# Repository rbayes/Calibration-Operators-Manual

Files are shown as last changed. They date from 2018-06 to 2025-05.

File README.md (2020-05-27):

# Calibration-Operators-Manual
An update to the calibration operator procedures for SNO+

Suggestions/Issues/Plans

Front Matter, (title page, linked table of contents) needs to be added.

May need to re-assess organisation of sections

## 2. Controls
- needs to be updated for the current calibration computer
- login information (passwords?)
- manmon (for external systems)

## 3. Manipulator
- needs update for hanger/bellows systems
- external systems (possibly) need to be highlighted
- double check that the computer system description is up to date

## 4. Manipulator Geometry
- Review "Global Coordinate System"
  - are all of the tables complete?
  - are they still correct?
- Does the context of the global geometry still make sense
  - Going from a UI mounted system to a I-beam mounted system
  - Should calibration system be defined wrt the PSUP
- Glovebox and UI description should be borrowed from the detector paper (early drafts)

## 5. Calibration Gas Systems
- Will need to have some comments about the cover gas system
- Specifications and UI cover gas monitoring will be required
  - Borrow from the detector paper and the TWiki
- Plans for URM cover gas required
- Comments on background mitigations and radon requirements

## 6. Laser
- Is the existing documentation sufficient
- Super Nova Calibration source?

## 7. Sources
- Need Scintillator sources (Laserball AmBe, Tagged, Untagged and Cherekov sources)
- Need external source specifications (AmBe, N16, Laserball)

## 8. Procedures
- Should separate Water Only, Scintillator Only, External and Generally applicable procedures into different sections
- Water Only
  - Mounting procedures
  - Internal N16 deployment
- External Deployment Procedures (Needs to be brought up to standards)
  - Mounting procedures (to be written)
  - N16
  - AmBe
  - Laserball 
- Scintillator (with adjustments)
  - Mounting procedures
  - Pump/purge procedures 
  - Cover gas maintenance
  - Source handling
  - AmBe / Encapsulated deployments (adapted from water) 
  - Cherenkov deployment (adapted from water)
  - Laserball deployments (adapted from water) 
- Applicable to all
  - Supernova source
  - DT generator
  - Laser procedures
  
## 9. Deployment Records?
- Would it be worth recording Run numbers, dates, run plans in the operators manual for future reference?
- Limit to one page summaries

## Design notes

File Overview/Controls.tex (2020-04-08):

Control of the calibration manipulator and the calibration laser is
done through the \textbf{calibration} computer running the \textbf{manip}
program which is a C++ program running on Linux. There are three ways
for the operator to send commands to \textbf{manip}:
\begin{itemize}
\item From the \textbf{calibration} console in the DCR.
\item From the \textbf{manmon} program running on a number of Linux
  boxes.
\end{itemize}
When changing source or adjusting equipment in the DCR, the console is
usually used. Otherwise the calibration operator usually interacts
with the manipulator through \textbf{manmon}. The manipulator can be
operated both from underground or from surface without any personnel
in the lab. There is also a monitoring program running on
\textbf{buffer1.sp.snolab.ca}. This program is called
\textbf{manip\_logger} which generates a json document containing the
current manipulator status and uploads the result to a couch database
on the \textbf{snopl.us} server. The resulting files may be viewed
from a web browser or downloaded directly.

\section{Controlling and Monitoring the Manipulator from manmon}
Nominal operatiorn of the mainipulator is through \textbf{manmon}
which is a Tcl/Tk program which runs on various Linux workstations on
site. Specifically the workstations

\paragraph{monug1} The workstation in the underground control room.
\paragraph{monag1} The workstation in the surface control room.
\paragraph{monlu1} The workstation in the Laurentian control room.

\textbf{manmon} provides a GUI interface to display the manipulator
data and to allow the Calibration Operator to move sources or operate
the calibration laser.

\subsection{Starting manmon}
\begin{enumerate}
\item Log on to \textbf{monug1} as \textbf{snoperator}
\item Go to the current manmon directory.
\begin{verbatim}
cd ~/manmon_3.00
\end{verbatim}
\item Start the \textbf{manmon} program by typing
\begin{verbatim}
manmon
\end{verbatim}
A GUI user interface will pop up Fig.~\ref{fig:manmonGUI}.
\item The GUI connects to the calibration computer automatically, but
  in case it does not, the connection may be forced by clicking on the
  \textbf{connect} button. A window will pop up (see
  Fig.\ref{fig:connect}) 
\end{enumerate}
The procedure is identical in the other control rooms.

\section{Controlling the Manipulator from the Console}
On the calibration computer, change to the directory
\begin{verbatim}
~/AVR32
\end{verbatim}
and run the program
\begin{verbatim}
./manip
\end{verbatim}
The basic commands are:
\paragraph{help}
\paragraph{list} lists all objects
\paragraph{logout} disconnects the tcp/ip connection
\paragraph{quit} exists program
Commands for the \verb+prototyp+ object (typically a source object
like \verb+laserball+, \verb+ambe+, \verb+li8+, etc.)

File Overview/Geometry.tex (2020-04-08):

\section{SNO+ Geometry and the Calibration System}

When using the manipulator the user is positioning the carriage pivot
in a coordinate system fixed to the AV. In SNO+ the acrylic vessel is
a free floating entity. Measurements by the detector are collected by
the PMT support structure which is fixed relative to the
cavity. Neither the PSUP nor the AV are expected to be possess a
mutual sensor, so the translation between the AV coordinate system and
the PSUP coordinate system must be independently measured. The
dimensions of the AV are given in Table~\ref{tab:avdims}.

\begin{table}
  \begin{center}
    \begin{tabular}{llll}
      \hline
      measurement & dim(in) & dim(cm) & source \\
      \hline
      height of DCR floor & 100'=1200'' & 3048.00 & definition \\
      height of global origin & 56' 7 1/2'' = 679.5'' & 1725.93 &
      design \\
      d(global origin to DCR floor) & 520.5'' & 1322.07 & calc. \\
      \hline
    \end{tabular}
  \end{center}
  \caption{Global Coordinate System}
  \label{tab:avdims}
\end{table}

\begin{table}
  \begin{center}
    \begin{tabular}{llll}
      \hline
      Measurement & Dim(in) & Dim(cm) & Source \\
      \hline
      Height of 10'' gate valve from UI & 13 & & \\
      Height of 6'' gate valve from UI & 8.25 & & \\
      \hline
      Height of Upper UI & 18.75 & & from Drawings\\
      Lower UI top flange width & 0.87 & & from Drawings\\
      Lower UI wall height & 28 & & from Drawings \\
      Lower UI bottom flange width & 0.75 & & measured \\
      UI height from top of lower UI bottom flange to top surface & 47.5625 & & measured \\
      Gap between AV and UI & 0.5 & & measured \\
      Height of UI top surface above AV center & 567.9725 & & calc. \\
      \hline
      URM1 source tube height to crosshairs & 41.85 & 106.3 & measured \\
      URM1 crosshair height & 609.8228 & 1548.95 & calc. \\
      URM2 source tube height to crosshairs & 40.812 & 103.66 & measured \\ 
      URM2 crosshair height & 609.9725 & 1549.33 & calc. \\
      URM3 source tube height to crosshairs & 43.819 & 111.3 & measured \\ 
      URM3 crosshair height & 607.5725 & 1542.23 & calc. \\
      \hline
    \end{tabular}
  \end{center}
  \caption{}
  \label{tab:UIheights}
\end{table}

\begin{table}
  \begin{center}
    \begin{tabular}{llll}
      \hline
      Measurement & AV height(in) & AV height(cm) & source \\
      \hline
      Laser level & & \\
      
      \hline
    \end{tabular}
  \end{center}
  \caption{Dimensions of the SNO+ detector.}
  \label{tab:avpsupmeas}
\end{table}

\begin{table}
  \begin{center}
    \begin{tabular}{llll}
      \hline
      measurement & dim (in)& dim (cm)& from \\
      Average Vessel Inner Radius & 236.38$\pm$0.23'' &
      600.41$\pm$0.58 & measurement\\ 
      Top of Chimney to AV bottom & 742.59$\pm$0.05'' &
      1886.18$\pm$0.13 & measurement\\ 
      Top of Chimney to AV centre & 506.16$\pm$0.12'' & 1285.65$\pm$0.30 &
      measured? \\
      Neck Ring gasket & 1/8'' & 0.3175 & measured \\
      Neck Ring plate & 3/8'' & 0.9525 & measured \\
      AV Centre to AV top plate & 506.66'' & 1286.92 & calculated \\
      DCR floor to AV top plate & 12.4375'' & 31.59 & measured/calculated\\
      \hline
    \end{tabular}
  \end{center}
  \caption{Dimensions of the SNO+ detector.}
  \label{tab:avpsupmeas}
\end{table}

There are multiple methods for the measurement of the AV with respect
to the AV. The first is a direct measurement of the top of the UI
relative to the PSUP anchors using a laser level. This requires
opening part of the light seal for the cavity so it is not something
that can be repeated with a high regularity. Measurements using
reflections of light from TELLIE has provided a very good measurement
of the position of the AV with respect to the PSUP. This analysis can
be repeated with the further TELLIE runs. Further measurements can be
completed from the analysis of changes in the tensions on the hold
down ropes although the initial lengths and positions are not well
understood. The results of these measurements are given in
Table~\ref{tab:avpsupmeas}.

The relative positions of the guide tube gate valves have been
measured with respect to the top of the AV. In the water phase the
gate valves from SNO were used due to the low tolerances of the gate
valves aquired for SNO+. These positions then give the total distance
of the source from the center of the detector given the height of the
source tubes. The measurements were conducted using a laser level and
a measuring tape and compiled in Table~\ref{tab:guidetubeheight}.

\begin{table}
  \begin{center}
    \begin{tabular}{cccccc}
      \hline
      Tube & X (cm)& Y (cm)& Enter PSUP & Z Leaves PSUP & Z Touches
      AV(cm)\\
      \hline
      1&361.00&193.04& 734.36& &446.91 \\
      2&-112.08& 104.14& 825.47& &586.44 \\
      3&-361.00& 193.04& 733.51& &446.91 \\
      4&-586.11& 207.96& 564.64& -564.64 & \\
      5&-586.11&-252.41& 546.23& -546.23 & \\
      6& 118.11&-119.38& 823.80& & 582.32\\
      \hline
    \end{tabular}
  \end{center}
  \caption{Calibration Guide Tube Locations.}
  \label{tab:guidtubeheight}
\end{table}

\section{Acrylic Vessel}
The thermal expansion coefficient for the acrylic is
\begin{math}
  6\times 10^{-5}\textrm{C}^{-1}
\end{math}
The design specs for the AV give the distance from the top of the neck
to the centre of the vessel at 23 C
\begin{verbatim}
42' 2 3/8''
\end{verbatim}
which is 506.375~cm and the nominal outside radius is
\begin{verbatim}
236.6''
\end{verbatim}
which is 600.964~cm with a nominal thickness of 2.15'' (5.461~cm).

This can be compared to the results found in SNO-STR-98-003 (R. Komar)
for actual measurements of the AV. Using the Komar measurements, the
nominal dimensions of the AV are given in Table~\ref{tab:}. On top of the AV
neck flange is a gasket (1/8'') and a stainless steel top plate
(3/8''). This gives a distance from the centre of the AV to the top
plate of,
\begin{math}
  506.16 + 1/8 + 3/8 = 506.66\textrm{in} = 1286.92\textrm{cm}
\end{math}

Recent measurements of the 

\section{Calibration Guide Tubes}

The locations of the calibration guide tubes in the Deck Clean Room
are shown in Fig.~\ref{fig:deckplan} and Fig.~\ref{fig:gtelev}. The
heights of the gate valves for the guide tubes as well as the heights
of the mounted source tubes at the cross hairs is given in
Table~\ref{tab:gtheights}.

\begin{figure}

  \caption{Deck plan of the DCR showing the positions of the guide
    tubes}
  \label{fig:deckplan}
\end{figure}

\begin{figure}

  \caption{Elevations of the calibration guide tubes}
  \label{fig:gtelev}
\end{figure}

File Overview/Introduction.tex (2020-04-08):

% \section{Introduction}

The calibration of the SNO+ detector can be divided into three
aspects:
\begin{enumerate}
\item Calibration of the low level electronics channels (ECA).
\item Calibration of the phototube timing (PCA).
\item Calibration of the detector's physics response.
\end{enumerate}
The low level electronics calibrations (ECA) are done via calibration
circuitry built into the electronics hardware and are not consider
further here. The scope of this document is the equipment and
procedures used to do the phototube calibrations (PCA) and the
multitude of physics calibrations.

The phototube and physics calibration of the SNO+ detector consists of
placing standard sources of light or radioactivity (gamma rays and
electrons) at known locations within the detector. These sources are
used to extract the calibration parameters for both the individual
phototubes (timing resolution, charge vs time, charge resolution,
efficiency) and bulk properties of the detector (wavelength dependent
light attenuation of materials, global detection efficiency).

SNO+ uses known optical and radioactive sources to measure the
calibrations. The optical sources include the \textbf{laserball} and
the \textbf{ELLIE} system while radioactive sources include the
\textbf{$^{16}$N Gamma Ray Source}, the \textbf{$^{8}$Li Cherenkov
  Source}, or the \textbf{$^{270}$Am$^{8}$Be}. Each source has unique
physical properties byt they all share the requirements of being
constructed of materials with little or no radioactivity (except for
the source material in the case of active sources). Specific sources
have been developed for both water and scintillator phases. The
\textbf{Calibration Manipulator System} positions the sources within
the SNO+ detector. The manipulator is a computer controlled system
that is designed to place a source within the acrylic vessel (AV) or
the water between the AV and the PSUP.

\section{Overview of the Calibration Apparatus}

The calibration systems in SNO+ are are situated in the Deck Clean
Room (DCR) in the SNO cavity at SNOLAB. The clean room exists to
minimize the amount of potential background contamination. The central
feature of the DCR is the Universal Interface (UI) to the AV that is
itself the centerpoint of the SNO+ experiment. The UI posseses three
gate valves through which sources may be deployed. Two of these gate
valves are typically occupied by source tubes which partially support
Umbilical Retrieval Mechanisms (URMs) which control the vertical
deployment of calibration sources. The apparatus is designed to
maintain the \textbf{Cover Gas} seal on the detector. Prior to opening
valves to the detector volume, airs is flushed out of the URMs with
pure N$_{2}$ gas derived from liquid nitrogen dewars located in the
Junction. The apparatus also maintains the light seal on the detector
allowing the deployment of sources with the detector turned on.

The URMs use electric motors and a pneumatic
piston to control the movement of a source by applying appropriate
tension on the central rope and umbilical. The URM is instrumented
with encoders and load cells so that the length and the tension on the
umbilical and central rope are known. In the ideal case for a single
axis deployment the tensions are balanced equally between the rope and
the umbilical. Controller boxes attached to the URMs are connected to
a central calibration computer via USB. A lifting mechanism moves the
URMs on and off of the UI and carts are used to move the URMs about
the DCR when they are not on the UI.

Three URMs are in use that were developed for SNO. URM1 was rebuilt to
deploy the Cherenkov source during water phase. Because of the larger
diameter of this source it must be deployed through the 10''
gatevalve. URM2 houses the laserball source and is also mounted on the
10'' gatevalve. Encapulated sources, such as the AmBe source, are
installed on URM2 using the laserball can as a platform, but the
laserball source is restored immediately after deployment. URM3 is the
permanent home of the $^{16}$N gamma ray source and is usually mounted
on the 6'' gatevalve.

For the scintillator phase a new URM1 has been developed with new
materials that are compatible with LAB and better gas systems to
reduce potential background contamination. This system differs
somewhat from the SNO calibration systems in the ways that it
interacts with the cover gas and is mounted on a double gate valve
system so that the URM may be purged more efficiently.

The control of the source positions are supplimented by side
ropes. These ropes are fixed to the inside of the AV and the tensions
are controlled through the use of motors with load cell and encoder
feed back. Sources ride along these ropes on pulleys so that the
relative tension between the central rope and two side ropes guide the
source within a plane. The side ropes are paired to guide the source
in the X-Z plane (using the East and West side ropes) or the Y-Z plane
(using the North and South side ropes). The side ropes are controlled
by the same computer system as the 

Further calibration can be conducted external to the AV. A system of
laser fibers are embedded in on the PSUP for the Embedded LED Laser
Injections Entity (ELLIE). This system 

\section{Contacts}

Below are names and phone numbers for people familiar with different
parts of the calibration system. However, if there is any question
about the state and safety of the system, contact the \textbf{On Call
  Expert} (OCE). Prior to any running of the manipulator the head of
the calibration group or his designate will indicate who is the On
Call Expert.

\section{Rules of (Dis)Engagement}

Chapter 9 of these procedures describe possible problems with the
manipulator system and how to correct them. Some problems are straight
forward and are of little consequence. These problems can be corrected
by the operator. Some problems are significant and the On Call Expert
(OCE) should be contacted before addressing them. The OCE is in turn
required to inform the Head of the Calibration Group of his designate
of any significant problem (here significant is defined as a problem
that could potentially put the manipulator system, the detector or the
scintillator at risk).

{\bf
  \begin{enumerate}
  \item Contact the OCE for any problems that the trouble shooting
    section indicate the OCE should be contacted.
  \item Contact the OCE if you have doubts about a procedure.
  \item Contact the OCE if you have had to execute any of the
    emergency shutdown procedures.
  \item Contact the OCE if any abnormal situation occurs.
  \end{enumerate}

}

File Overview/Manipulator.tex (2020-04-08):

The SNO+ calibration manipulator is a positioning device used to place
calibration sources inside the AV of the SNO+ detector or down
calibration guide tubes in the region between the AV and PSUP. By
using a system of three ropes; a central rope and two dside ropes, the
manipulator is able to position a source on either an east-west (X-Z) or
north-south (Y-Z) plane inside the AV. About 3/4 of the plane inside
the AV can be reached by the manipulator, while the remaining quarter
is not accessible due to physical limits of the manipulator system
imposed by the geometry. In addition to the manipulator ropes, there
is an umbilical attached to the manipulator that provides the
necessary services for the source, such as electrical signals, fibre
optics or gas lines.

Each calibration source is stored in an Umbilical Retrieval Mechanism
(URM) prior to deployment. A URM consists of a pair of blocks for
taking up the source \textbf{Umbilical} used to provide services to
the source and a \textbf{central rope} used to support the weight of
the source. Below the URM is the \textbf{source tube} which is a 4'
long stainless steel pipe used to store sources when not deployed in
the vessel. Normally, the URM and source tube are mounted on a
calibration port on the \textbf{universal interface} located directly
over the neck of the acrylic vessel. When not in use, the source is
stored in the source tube and a gate valve on the UI seals off the
detector. The central rope in the URM is instrumented with a
\textbf{shaft encoder} which determines the length of rope played out
and a \textbf{load cell} used to measure the tension in the rope. The
umbilical is similarly instrumented.

The layout of the system is shown schematically in
Fig.\ref{fig:manipschema}.

\paragraph{Anchor Blocks}
Each side rope can be thought of as attached at two points (not
exactly true). At the feedthrough where it comes through the UI and at
the \textbf{anchor block} in the AV which is located just above the AV
equator. The end of the rope at the anchor block is fixed abd by
playing the rop in or out through the UI feedthrough, the calibration
source is moved about the AV.

\paragraph{Calibration Guide Tubes}
In addition to deploying sources through the glovebox into the center
of the AV, it is possible to deploy sources through 6 calibration
guide tubes into the cavity water volume between the AV and the
PSUP. These guide tubes are located on the floor of the DCR and are
sealed with gate valves.

\paragraph{Carriage and Weight}
Attached to each calibration source is a carriage and a weight. The
carriage provides attachment points for the central rope and umbilical
and has pullies that the side ropes go around. The weight cylinder is
a stainless steel tube containing lead. The manipulator requires a
miniumum weight for each source to function properly (in particular to
give the sources negative bouyancy) and the wieght cylinder provides
this.

\paragraph{Deck Clean Room(DCR)}
The DCR is the room centered on the deck. Most of the calibration
equipment is located inside the DCR. The DCR is kept clean and has
relatively few airborn particles compared to the rest of the lab. The
clean conditions are maintained to prevent introduction of radioactive
contamination into the detector during the deployment of sources.

\paragraph{Universal Interface (UI)}
The universal interface is a cylindrical box visible in the center of
the DCR through which all of the services into the AV are routed using
a large number of valves and flanges. Sensors, maintained by the
scintillator group to monitor the AV levels, are installed on the UI
alongside the three ports upon which the calibration sources may be
mounted. Additionally, the side rope motor boxes and load cell boxes
are mounted on the UI. The side ropes are attached to the manipulator
carriage of a source using glove ports on the sides of the UI. These
glove ports maintain the darkness within the AV and the integrity of
the radon free cover gas that caps the AV.

\paragraph{Rubbing Ring}
The rubbing ring is an acrylic ring located just below the neck of the
AV inside the target material volume. When the manipulator positions a
source off the central axis, the manipulator ropes and the source
umbilical are pulled to the side of the AV neck. The rubbing rung
provides a wearing surface for the ropes.

\paragraph{Side Rope Motor Mounts}
The spooling mechanisms for the side ropes are mounted on the UI. The
side rope motor boxes are connected to the AV cover gas through VCR
fittings to extension boxes which also conduct the side ropes from the
mechanism to the AV. The motor boxes themselves consist of a motor
driven spool system instrumented with a loadcell to measure the rope
tension and a shaft encoder to measure the rope length. There are four
side ropes, North, South, East and West which are operated in pairs to
allow positioning of the source inside the AV on and East-West or a
North-South plane.

\paragraph{Source Tube}
The stainless steel tube connecting the URM to the calibration
port. The calibration source is parked in the source tube when not
deployed in the detector.

The manipulator carriage and weight assembly is shown schematically in
Fig.~\ref{fig:mancarriage}. It consists of the carriage to which the
central rope is attached. The umbilical passes through the carriage
neck, through the weight assembly into the source. The side ropes are
not attached to the carriage, by rather pass around pullies mounted on
the pully bar. The pully bar and carriage neck are free to rotate
about the pivot. At different positions in the AV the pully bar and
carriage neck will be at different orientations while the weight
assembly and source will always hang vertically below the pivot.

The weigth consists of a stainless steel torus filled with lead. The
lead is potted into the weight cylinder with silicone and then capped
with the cylinder end plate with is sealed with o-rings. Sources are
usually attached to the weight cylinder using the extension tube.

\section{Manipulator Control System}

The manipulator is controlled by the \textbf{calibration} computer
which is a CENTOS Linux PC running a C++ program called manip. The
manip program interacts with the manipulator hardware by controlling a
stepper motor for each axis to change the length of the rope or
umbilical. A shaft encoder on each axis measures the length and a
loadcell measures the tension. The shaft encoders and load cells are
connected to \textbf{controller boxes}, one per two axes. Inside the
controller box is a set of three AVR boards, two to control an axis
(stepper motor, shaft encoder and load cell) and one to concentrate
the data and communicate with the calibration computer via USB. Each
controller box has a unique digital address which is identified as one
of 12 AVR boards. The hub currently in use allows for the use of four
control units at any given time which allows for the four side rope
motor boxes and two URMs to be connected simultaneously. The
N$_{2}$/dye laser is run using the same AVR boards, however it is
connected via an independent USB cable to the calibration computer.

\section{Modes of Source Deployment}

\subsection{Single Axis Deployment}

Sources can be deployed in a single axis mode which consists of
lowering a source straight down from the URM on just the central rope
and umbilical. The horizontal position of the source is determined by
the location of the URM. The vertical position of the source is
determined by the measured length of central rope played out. The
single axis deployment mode is useful for operation along the central
axis of the detector and for deployment of sources down the guide
tubes.

\subsection{Three Axis Deployment}

The main purpose of the manipulator however, is to deploy a source off
the central axis of the detector inside the acrylic vessel. This is
done attaching two side ropes to the manipulator carriage once it is
deployed into the glovebox. The side ropes are attached at one end to
anchor blocks in the AV are anchored at the other end by feedthroughs
on the glovebox. The side ropes go over pullies on the manipulator
carriage. Once the source is lowered into the vessel, it can be pulled
off the central axis by shortening one side rope and lengthening the
other. Because only two side ropes are attached at a time, the source
can only be moved in a plane. There are two sets of side ropes
allowing motion in an east-west plane or a north-south plane. The side
ropes are instrumented in the same fashion as the central rope with
the side rope motor mounts located on the UI. The ropes pass through
steel tubes, thence to extension boxes containing auxiliary pullys and
into the AV.

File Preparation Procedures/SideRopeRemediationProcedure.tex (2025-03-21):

\documentclass[11pt]{article}

\usepackage{geometry}                % See geometry.pdf to learn the layout options. There are lots.
\geometry{letterpaper}                   % ... or a4paper or a5paper or ... 
%\geometry{landscape}                % Activate for for rotated page geometry
%\usepackage[parfill]{parskip}    % Activate to begin paragraphs with an empty line rather than an indent
\usepackage{graphicx}
\usepackage{amssymb}
\usepackage{epstopdf}
%\usepackage{enumitem}
\usepackage{ulem}
\DeclareGraphicsRule{.tif}{png}{.png}{`convert #1 `dirname #1`/`basename #1 .tif`.png}
\usepackage{caption}
\usepackage{subcaption}

\title{Siderope O-ring Remediation}
\author{Ryan Bayes}
\date{\today; V4}

\begin{document}
\maketitle
\section{Introduction}
The side rope boxes are a part of the SNO+ calibration system  consisting of four large motor boxes each containing the rope spools coupled to an external motor, and connected to the UI through a 1/2 inch tube by way of one of four load cell boxes. As such, they are integrated into the SNO+ UI cover gas space.  Two of the motor boxes, the North Motor box and East Load Cell box seals have not shown leaks with a vacuum leak checker in excess of $10^{-4}$ mbar L/s where the expectation is that the leak should be less than $10^{-7}$ mbar L/s. Problems have also been observed in both the South motor box and load cell boxes. The results of the previous leak checking campaigns are shown in table \ref{tab:leakCheck}.

	\begin{table}
	\caption{Summary of previous leak checking campaigns as applied to the calibration side rope systems}
	\label{tab:leakCheck} 
	\begin{center}
	\begin{tabular}{|r|c|c|c|}
	\hline
	Feature & Status & Leak (mbar L/s)& Date\\\hline
	East and west motor box & good & $< 2\times10^{-8}$ & June 2023 \\
	West load cell box seal & good & $< 10^{-10}$ & June 2023 \\
	South motor box outer seal & pass & $5\times10^{-7}$ & June 2023 \\
	South motor box inner seal & fail &  $1.4\times10^{-5}$ & July 2023 \\
	South exten. box outer seal & fail &  $< 10^{-5}$ & June 2023 \\
	South exten. box inner seal & pass &  $2\times10^{-9}$ & July 2023 \\
	North motor box & fail &  $ > 10^{-4}$ & Oct 2019 \\
	North load cell box & pass&  $ < 10^{-9}$ & June 2023 \\
	East load cell box seal & fail & $ > 10^{-4}$ & Oct 2019 \\
	\hline
	\end{tabular}
	\end{center}
	\end{table}
	
Plastic bags flushed with nitrogen have been put over the boxes and this has reduced the radon levels somewhat, but the current background load in the detector is not reasonable. For this reason a more active approach to correcting this problem must be taken. The hypothesis is that there is something wrong with one or both of the o-rings that constitute the motor box seals. To remedy this problem the o-rings must be inspected and, if necessary, replaced. This procedure outlines the methods needed to conduct an o-ring inspection and replacement in a way that reduces radon ingress into the detector as much as possible.

\section{Definitions}
\begin{itemize}
\item {\bf AV}; Acrylic Vessel - The centre of the SNO+ detector containing the active scintillator volume
\item {\bf AV neck} - A 7 metre long cylinder that connects to the spheroidal main body of the AV. 
\item {\bf UI}; Universal interface - The cap on the top of the AV neck consisting of the lower UI through which tubes for recirculation and extracting samples from the AV are connected, and the upper UI through which ports for gas lines, level sensors and calibration equipment exist. 
\item {\bf DCR}; Deck clean room - a tent in the centre of the SNO+ deck to isolate activities about the UI that may introduce contamination into the experiment from the rest of the lab. Is equipped with multiple hepa filters to circulate and clean the air that passes into the facility. 
\item {\bf Bubblers} - Three gas lines that run into the UI through a bubbler flange which use gas pressure to determine the fluid level in the AV. 
\item {\bf Neck tubes} - PMTs installed on the UI to veto events suspected of appearing in the neck. Contained in steel top-hats with a coaxial electrical feedthrough on top. 
\item {\bf Radon monitor} - A 3 m$^{3}$ vacuum vessel used to measure levels of radon daughters in the cover gas volume. It is connected to the UI cover gas through a 1" diameter bellows hose. 
\item {\bf Side rope motor box} - One of four boxes cantilevered off of the UI. Used to adjust the tension on the ropes used to guide sources in a 2-dimensional plane in the UI (either XZ or YZ). Necessarily connected to the UI cover gas through a 1/2" tube containing the side rope. All four motor boxes are equipped with quick connects to facilitate a clean connection to the UI cover gas space.
\item {\bf Side rope load cell box} - One of four boxes used to align the side rope with a feed through to enter the UI. So called because the original design called for a load cell to be included to provide a secondary measurement of the rope tension. The load cell is not connected into the manipulator system, however. Each load cell box is connected to the siderope motor box via a 1/2" inch tube with VCR connections on both ends. Each is further connected to the UI cover gas through the rope feedthrough. Two load cell boxes (East and South) are equipped with valves to allow for clean connections to the UI cover gas.  
\end{itemize}

\begin{figure}[htbp]
\begin{center}

\caption{The UI with pink plastic nitrogen bags installed on the UI over the North Motor Box and the East Load cell box.}
\label{fig:UI}
\end{center}
\end{figure}

\begin{figure}[htbp]
\begin{center}

\caption{One of the motor boxes with an acrylic window installed to see the interior mechanisms.}
\label{fig:eastrope}
\end{center}
\end{figure}

section{Personnel}
\begin{itemize}
\item Task Lead: Ryan Bayes
\item Second: Matt Depatie
\item Cover gas expert: Aleksandra Bialek
\item Cover gas monitor: Parmesh Ravi (training required)
\end{itemize}

\section{Parts and Equipment List}
\begin{itemize}
	\item 2$\times$ TEV o-ring; 604mm $\times$ 2.6 mm
	\item 2$\times$ TEV o-ring; 596mm $\times$ 2.6 mm
	\item 2$\times$ TEV o-ring; 456mm $\times$ 2.6 mm
	\item 2$\times$ TEV o-ring; 449mm $\times$ 2.6 mm
	\item 88 hex cap screws for Motor box replacements 20mm $\times$ 1/4", ultrasonically cleaned
	\item 1 (or more) 3/16" Allen key
	\item 1 ratchet with 3/16" hex bit
	\item 1 1/4" torx hex bit (for removing stripped cap screws)
	\item 1 vice grip
	\item 1 mallet
	\item Helium leak checker
	\item Helium spray bottle (filled)
	\item Nitrogen source
	\item Flow meter
	\item Nitrogen regulator
\end{itemize}

\section{Risks and Mitigation}

The risk to workers through this procedure is extremely low. Workers should conduct themselves with the following considerations 
\begin{itemize}
\item  A potential oxygen deprivation hazard due to  exposure to the cover gas. This can be mitigated by ensuring that workers keep their faces well away from open ports to the UI at all times (low risk, low severity)
\item Workers must be aware of pinch points as the purpose of the activity requires sealing heavy metal steel surfaces against each other. (medium risk, low severity)
\item The lids to the motor boxes are heavy, so steps to prevent musculo-skeletal distress should be taken (get help as required and potentially using mechanical assistance if necessary). (medium risk, low severity)
\end{itemize}

\subsection{Radon Mitigation}\label{ss:radmit}
The primary risks with these procedures are to the detector itself through radon ingress. The solution to this is to set up a monitored UI flushing path. This involves
	\begin{enumerate}
	\item Connect one of the load cell gas ports (the valve on the South or East load cell boxes) to a nitrogen source (preference is for a nitrogen bottle) through a regulator and a flow meter with a shut-off valve inside the DCR.
	\item Connect an outflow line using a quick connect, a 1/4" teflon line and a 1/4" check valve and a pump.
	\item Start monitoring the cover gas bag size and UI dp using Delta V. This should be done by a user not directly doing the work on the UI with a laptop situated in the DCR garage.
	\item Start the nitrogen flow into the UI with a pressure less than 10 psi, and a flow less than 5 L/min
	\item Match the nitrogen inflow with the pump outflow pressure. The UI dp must be in a range of $\pm$ 0.05 psi as read out on delta V using DPT-005. Adjustments to the dp should be made by using the valve before the flow meter to throttle the gas flow.
	\item Continue monitoring the UI dp through the UI procedures.
	\item The nitrogen flow should continue for 30 minutes after the motor box is closed and sealed.
	\item Turn off the nitrogen flow followed by the pump in close sequence.
	\item Disconnect the pump from the motor box and move to the next motor box. 
	\end{enumerate}
To reduce the volume that can be exposed to contamination the radon monitor and UI cover gas bags should both be valved off. Both valves are metal seated valves, the operation of which requires a properly set and calibrated torque wrench as part of the closing procedure. The specifications for both are recorded on the valves themselves. 

\section{Procedure}

\subsection{Pre-Requisites}
To conduct this procedure the environment must be prepared. This includes
	\begin{itemize}
	\item The DCR must be well cleaned. This includes vacuuming the floors, wiping down the DCR walls, and wiping down surfaces including shelves and UI
	\item Pass swipe tests on surfaces in the DCR such as the UI, shelving, and URMs.
	\item A benchmark of fewer than 200, 0.5$\mu$m dust counts per $m^{3}$ per second must be achieved in the DCR air.
	\item Prepare all tools for use in a secure location away from the UI, preferably on a trolley for ease of access. This includes wiping down all tools to reduce the chance of dust getting into the UI, ensuring that the required machine screws are available, and wiping down the o-rings.
	\end{itemize}
These cleaning activities and tests must be done on the days prior and the day of the procedure. If at any point the tests fail, cleaning should be redone, and the tests should be done again. 

On the day of the o-ring replacement, the o-rings themselves should have a liberal amount of vacuum grease applied to help them stick in the o-ring grooves during installation.

\subsection{Emergency Procedures}

If there is an all stations call with a side-rope box open
\begin{itemize}
\item Place a cover (the remnants of the North box nitrogen bag should be sufficient) over the open box to provide a dust shield.
\item Change the nitrogen inflow to use a dewar (if using a bottle, switch to using the international). 
\item Maintain the nitrogen flow and monitor it from refuge through the all stations call
\end{itemize}

If there is an all stations call with a side-rope box cover partially in place (i.e. subset of screws installed) or between o-ring replacement procedures. 
\begin{itemize}
\item Change the nitrogen inflow to use a dewar (if using a bottle, switch to using the international). 
\item Maintain the nitrogen flow and monitor it from refuge through the all stations call
\end{itemize}

Assess the situation at the end of the all stations, and determine if work can resume, or if the UI must be put into a safe state (i.e. Cover-gas bags reconnected) until next the working day.

\subsection{Evaluate and Replace North Motor Box Seals}

\newcounter{northcounter}
\newcommand\north{\stepcounter{northcounter}\thenorthcounter}

\begin{tabular}{|c|c|p{15cm}|}
\hline
\north & & Turn off the radon monitor pump and valve off the radon monitor recirculation line. Disconnect the radon monitor return line from the East motor box. Valve off the radon monitor from the UI using the valve on the West side of the radon monitor. \\
\hline\north& & Place the detector at low voltage. \\
\hline\north & & Stop the flow into the UI nitrogen bags. Remove the bags from North motor box and East load cell box.\\
\hline\north & & Connect N$_{2}$ source to UI to "flush" UI as described in subsection \ref{ss:radmit}. The in-flow line should be connected to the South load cell box with the out-flow line connected to the North Motor box quick connect. \\
\hline\north & & Disconnect two of the cover gas bags from the UI. A dedicated worker must monitor the UI dp via Delta V and adjust the nitrogen inflow as necessary. That worker should balance the inflow and outflow to the UI with the two bags disconnected. Once he nitrogen flow is balanced, the last bag can be disconnected. \\
\hline\north & & Remove the cover from the North motor box by systematically removing the screws from the cover. One or more screws may be stripped, so use the torx bit or vice grip to extract those cap screws.\\ 
\hline\north & & Examine the  o-rings. Check if the o-rings are inside the groove as intended or escaped the groove (if possible). If the o-ring is outside the groove, the o-ring is likely crushed and will need to be replaced. If the o-ring was inside its groove, check for obvious damage. If there is any damage, replace the outer o-ring. The inner TEV o-ring must be replaced. \\
\hline\north & & With one worker holding the box cover, a second worker starts installing the new screws in the cover at the corners. Once the corner screws are started, the cover is eased into place, taking care that the o-ring does not roll or leave their groove. The corner screws tighten should be then be tightened and the remaining screws can be put into place. All the screws should be tightened using a star pattern.\\
\hline\north & & Check the seal using the helium leak checker. 
\begin{itemize}
\item Open one of the inter-o-ring seal VCR ports and connect it to the leak checker (ensuring that the opposing VCR plug is in tact). 
\item Start the leak checker. Once the turbo pump activates (allowing "fine" measurements to be taken) systematically spray each of the edges with helium  looking for the maximum leak rates on each edge. 
\item If a good vacuum cannot be achieved by the leak checker or the leak rate on any particular edge is less that 10$^{-7}$ mbar L/s, stop the leak checker and tighten the screws again. 
\item Repeat as necessary
\end{itemize}
\\
\hline\north & & Once the seal is satisfactory and the flush has continued for 30 minutes, disconnect the flush out-flow line from the North motor box and move it to the East Motor box. \\
\hline
\end{tabular}

\subsection{Evaluate and Replace East Load Cell Box Seals}
\newcounter{eastcounter}
\newcommand\east{\stepcounter{eastcounter}\theeastcounter}
\begin{tabular}{|c|c|p{15cm}|}
\hline\east & & Remove the bag from the East load cell box. \\
\hline\east & & Remove the cover from the East load cell box by systematically removing the screws from the cover. One or more screws may be stripped, so use the torx bit or vice grips to extract those cap screws.\\ 
\hline\east & & Examine the  o-rings. Check if the o-rings are inside the groove as intended or escaped the groove (if possible). If the o-ring is outside the groove, the o-ring is likely crushed and will need to be replaced. If the o-ring was inside its groove, check for obvious damage. If there is any damage, replace the outer o-ring. The inner TEV o-ring must be replaced. \\
\hline\east & & With one worker holding the box cover, a second worker starts installing the new screws in the cover at the corners. Once the corner screws are started, the cover is eased into place, taking care that the o-ring does not roll or leave their groove. The corner screws tighten should be then be tightened and the remaining screws can be put into place. All the screws should be tightened using a star pattern.\\
\hline\east & & Check the seal using the helium leak checker. 
\begin{itemize}
\item Open one of the inter-o-ring seal VCR ports and connect it to the leak checker (ensuring that the opposing VCR plug is in tact). 
\item Start the leak checker. Once the turbo pump activates (allowing "fine" measurements to be taken) systematically spray each of the edges with helium  looking for the maximum leak rates on each edge. 
\item If a good vacuum cannot be achieved by the leak checker or the leak rate on any particular edge is less that 10$^{-7}$ mbar L/s, stop the leak checker and tighten the screws again. 
\item Repeat as necessary
\end{itemize}
\\
\hline\east & & Once the seal is satisfactory and the flush has continued for 30 minutes, disconnect the flush out-flow line from the East motor box and move it to the South Motor box. \\
\hline\east & & Turn off the nitrogen source. Close the valve and move the nitrogen source line from the South Load cell box to the East Load cell box. \\
\hline\east & & Assess time remaining in shift. 
	\begin{itemize}
	\item If there more than half the shift remains, continue work on the South Motor Box and Load Cell Box. 
	\item If less than half the shift remains, do not re-establish the nitrogen flow and reconnect the cover-gas bags. Resume work (re-establish the nitrogen flow and disconnect the cover gas bags) on the following shift. 
	\end{itemize}
\\

\end{tabular}

\subsection{Evaluate and Replace South Motor Box and Load Cell Box Seals}
\newcounter{southcounter}
\newcommand\south{\stepcounter{southcounter}\thesouthcounter}

\begin{tabular}{|c|c|p{15cm}|}
\hline\south & & Remove the cover from the South motor box by systematically removing the screws from the cover. One or more screws may be stripped, so use the torx bit  or vice grip to extract those cap screws.\\ 
\hline\south & & Examine the  o-rings. Check if the o-rings are inside the groove as intended or escaped the groove (if possible). If the o-ring is outside the groove, the o-ring is likely crushed and will need to be replaced. If the o-ring was inside its groove, check for obvious damage. If there is any damage, replace the outer o-ring. The inner TEV o-ring must be replaced. \\
\hline\south & & With one worker holding the box cover, a second worker starts installing the new screws in the cover at the corners. Once the corner screws are started, the cover is eased into place, taking care that the o-ring does not roll or leave their groove. The corner screws tighten should be then be tightened and the remaining screws can be put into place. All the screws should be tightened using a star pattern.\\
\hline\south & & Check the seal using the helium leak checker. 
\begin{itemize}
\item Open one of the inter-o-ring seal VCR ports and connect it to the leak checker (ensuring that the opposing VCR plug is in tact). 
\item Start the leak checker. Once the turbo pump activates (allowing "fine" measurements to be taken) systematically spray each of the edges with helium  looking for the maximum leak rates on each edge. 
\item If a good vacuum cannot be achieved by the leak checker or the leak rate on any particular edge is less that 10$^{-7}$ mbar L/s, stop the leak checker and tighten the screws again. 
\item Repeat as necessary.
\end{itemize}
\vspace{-0.2cm}
\\
\hline\south & & Remove the cover from the South load cell box by systematically removing the screws from the cover. One or more screws may be stripped, so use the torx bit, or a pair of vice grips, to extract those cap screws.\\ 
\hline\south & & Examine the  o-rings. Check if the o-rings are inside the groove as intended or escaped the groove (if possible). If the o-ring is outside the groove, the o-ring is likely crushed and will need to be replaced. If the o-ring was inside its groove, check for obvious damage. If there is any damage, replace the o-ring. The inner TEV o-ring must be replaced in any case. \\
\hline\south & & With one worker holding the box cover, a second worker starts installing the new screws in the cover at the corners. Once the corner screws are started, the cover is eased into place, taking care that the o-ring does not roll or leave their groove. The corner screws tighten should be then be tightened and the remaining screws can be put into place. All the screws should be tightened using a star pattern.\\
\hline\east & & Check the seal using the helium leak checker. See above steps.\\
\hline
\end{tabular}

\subsection{Procedure time estimates}
For guidance, it is expected that the following procedures will take the following time. 
\begin{itemize}
\item Remove cover screws: 5 minutes
\item Time with direct gas path open to UI: 2-5 minutes to examine, remove, and replace the o-ring
\item Replace cover screws: 10 - 15 minutes
\item Flush the side rope box 30 minutes
\item Leak test the side rope box 30 minutes (can be done at the same time as flushing).
\end{itemize}
Maximum time of each segment of the procedure: 1 hour. Maximum total expected working time: 4 hours. Given that setting up the cover gas flow should take no more than 30 minutes, These procedures are expected to be completed within one shift. However a second shift should be planned for contingency in case some steps take longer than estimated.

\section{Clean up}
\newcounter{cleancounter}
\newcommand\clean{\stepcounter{cleancounter}\thecleancounter}
\begin{tabular}{|c|c|p{14cm}|}
\hline\clean & & Once the seal is satisfactory and the flush has continued for 30 minutes, disconnect the flush out-flow line from the South Motor box and turn off the pump. Turn off and disconnect the nitrogen source (after sealing the valve).\\
\hline\clean & & Ensure that all of the old screws are secured and stored in anticipation of disposal. \\
\hline\clean & & Put all of the tools away in the tool box. \\
\hline\clean & & Clean the DCR walls, floors and surfaces. \\
\hline\clean & & Reconnect the Radon monitor recirculation path, open the path valve and restart the pump. \\
\hline\clean & & Return the detector to high voltage. \\
\hline\clean & & Leave the DCR and turn off the lights. \\
\hline 
\end{tabular}

\section{Afterwards}
Following the completion of the seal replacement a few follow-up activities must be completed.
\begin{itemize}
\item The levels in the radon monitor must be evaluated actively over the following week. The radon that is introduced by this procedure should decrease with the radon half-life of 3.9 days. A longer half life indicates a further leak in the detector that should be identified.
\item The vacuum leak checker should be run on the seals again after letting the motor box seals rest for a period of two weeks. This should verify that the seals can be maintained over time with minimal retorquing. 
\item The inter-o-ring space should be connected to a nitrogen flow if there is evidence of a leak. The sealing process will not be repeated, but, depending on the nature of the leak, flushing the seal with nitrogen could reduce the radon contamination across. 
\item The bags around the neck tubes should be checked. The nitrogen flow to these bags should not be one for the first two weeks of radon monitor observations. The flow to the bags can be reinstated after the radon monitor levels find their "new normal".  
	\begin{itemize}
	\item If the flow effectively inflates the bags, and the radon monitor levels reduce over the following two weeks, then it is likely that the neck tubes are a radon leak source. 
	\item If the bags inflate, but there is no change in the radon monitor levels, then it is likely that the neck tubes are not a radon source in the UI. 
	\item If the bags do not inflate the bags should be replaced and the test conducted as described above. 
	\end{itemize}
If the neck tubes are shown to be a radon source then a more permanent solution to seal the neck tube feedthroughs should be identified.
\end{itemize}
	
\begin{figure}[htbp]
\begin{center}
	\begin{subfigure}{0.45\textwidth}
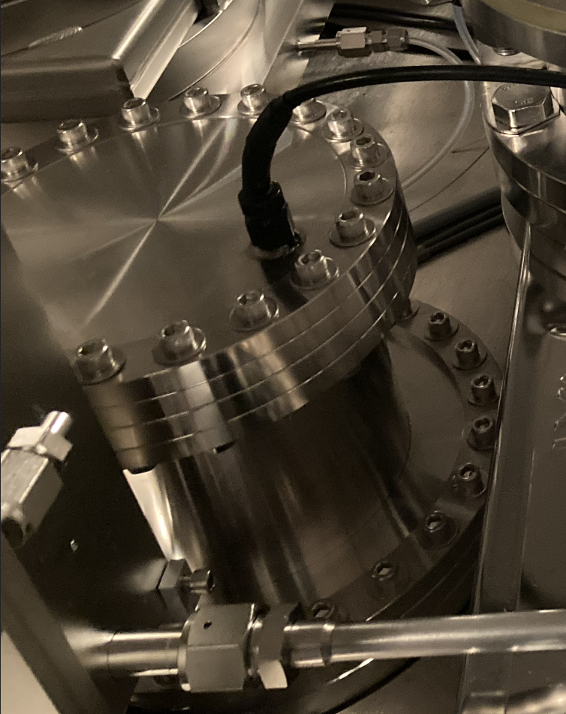
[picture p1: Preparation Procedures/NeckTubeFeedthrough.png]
	
	\caption{The Neck Tube feedthroughs.}
	\label{fig:necktubefeedthrough}
	\end{subfigure}
	\begin{subfigure}{0.45\textwidth}
	
	\caption{West neck tube bag}
	\label{fig:necktubebag}
	\end{subfigure}
\caption{Neck tubes feedthroughs are a potential source of radon in the UI that should be evaluated after the motor box seals are remediated.}
\label{fig:necktubes}
\end{center}
\end{figure}

\end{document}

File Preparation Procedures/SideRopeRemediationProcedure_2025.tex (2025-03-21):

\documentclass[11pt]{article}

\usepackage{geometry}                % See geometry.pdf to learn the layout options. There are lots.
\geometry{letterpaper}                   % ... or a4paper or a5paper or ... 
%\geometry{landscape}                % Activate for for rotated page geometry
%\usepackage[parfill]{parskip}    % Activate to begin paragraphs with an empty line rather than an indent
\usepackage{graphicx}
\usepackage{amssymb}
\usepackage{epstopdf}
%\usepackage{enumitem}
\usepackage{ulem}
\DeclareGraphicsRule{.tif}{png}{.png}{`convert #1 `dirname #1`/`basename #1 .tif`.png}
\usepackage{caption}
\usepackage{subcaption}

\title{Siderope O-ring Remediation}
\author{Ryan Bayes}
\date{\today; V5}

\begin{document}
\maketitle
\section{Introduction}
The side rope boxes are a part of the SNO+ calibration system  consisting of four large motor boxes each containing the rope spools coupled to an external motor, and connected to the UI through a 1/2 inch tube by way of one of four load cell boxes. As such, they are integrated into the SNO+ UI cover gas space.  Two of the motor boxes, the North Motor box and East Load Cell box seals have not shown leaks with a vacuum leak checker in excess of $10^{-4}$ mbar L/s where the expectation is that the leak should be less than $10^{-7}$ mbar L/s. Problems have also been observed in both the South motor box and load cell boxes. The results of the previous leak checking campaigns are shown in table \ref{tab:leakCheck}. The North motor box, East load cell box and South siderope system o-rings have been replaced. Of these the North Motor box and the South Load cell box show leaks. It is suspected that the North Motor box issues are due to a warped flange or cover, and so it is unlikely that further improvements beyond activly feeding nitrogen through the flange. Some residue was observed on the flange of the South load cell box when those o-rings were replaced, so the goal at this time is to remove this residue and replace the o-rings on this box a second time before replaceing the cover and leak checking the motor box.  

\begin{table}
  \caption{Summary of previous leak checking campaigns as applied to the calibration side rope systems}
  \label{tab:leakCheck} 
  \begin{center}
    \begin{tabular}{|r|c|c|c|}
      \hline
      Feature & Status & Leak (mbar L/s)& Date  \\\hline
      East and west motor box & good & $< 2\times10^{-8}$ & June 2023 \\
      West load cell box seal & good & $< 10^{-10}$ & June 2023 \\
      South motor box outer seal & pass & $5\times10^{-7}$ & June 2023 \\
      South motor box inner seal & pass &  $1.4\times10^{-7}$ & July 2024 \\
      South exten. box outer seal & fail &  $3\times 10^{-5}$ & June 2024 \\
      South exten. box inner seal & pass &  $2\times10^{-9}$ & July 2023 \\
      North motor box & fail &  $ > 10^{-4}$ & May 2023 \\
      North load cell box & pass&  $ < 10^{-9}$ & June 2023 \\
      East load cell box seal & fail & $ > 10^{-4}$ & Oct 2019 \\
      \hline
    \end{tabular}
  \end{center}
\end{table}

The measures taken during the previous seal remediations were demonstrated to be successful at suppressing radon to well below DCR background levels. This procedure is described in section \ref{ss:radmit}. Figure \ref{fig:radmon} shows the radon monitor data collected between April and July of 2025. For reference Deck air injected into the radon monitor directly will produce a rate of 1.3 Hz, whereas the expected operation produced an increase in rate of approximately 0.01 Hz; more than a factor of 100 reduction.

\begin{figure}
  \begin{center}
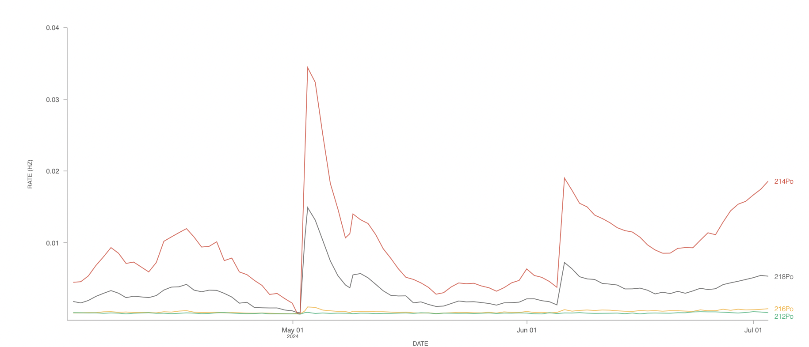
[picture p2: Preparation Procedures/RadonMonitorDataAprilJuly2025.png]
    
  \end{center}
  \caption{Radon Monitor data collected between April and July of 2024, showing the first siderope remediation procedure (May 1, 2024) and the second (June 5, 2024). The second is closer in scope to the procedure proposed here.}
  \label{fig:radmon}
\end{figure}

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

\begin{figure}[htbp]
\begin{center}

\caption{The UI with pink plastic nitrogen bags installed on the UI over the North Motor Box and the East Load cell box.}
\label{fig:UI}
\end{center}
\end{figure}

\begin{figure}[htbp]
\begin{center}

\caption{One of the motor boxes with an acrylic window installed to see the interior mechanisms.}
\label{fig:eastrope}
\end{center}
\end{figure}

section{Personnel}
\begin{itemize}
\item Task Lead: Ryan Bayes
\item Second: Matt Depatie
\item Cover gas expert: Aleksandra Bialek
\item Cover gas monitor: Clara Dima (training required)
\end{itemize}

\section{Parts and Equipment List}
\begin{itemize}
	\item 2$\times$ TEV o-ring; 604mm $\times$ 2.6 mm
	\item 2$\times$ TEV o-ring; 596mm $\times$ 2.6 mm
	\item 2$\times$ TEV o-ring; 456mm $\times$ 2.6 mm
	\item 2$\times$ TEV o-ring; 449mm $\times$ 2.6 mm
	\item 88 hex cap screws for Motor box replacements 20mm $\times$ 1/4", ultrasonically cleaned
	\item 1 (or more) 3/16" Allen key
	\item 1 ratchet with 3/16" hex bit
	\item 1 1/4" torx hex bit (for removing stripped cap screws)
	\item 1 vice grip
	\item 1 mallet
	\item Helium leak checker
	\item Helium spray bottle (filled)
	\item Nitrogen source
	\item Flow meter
	\item Nitrogen regulator
\end{itemize}

\section{Risks and Mitigation}

The risk to workers through this procedure is extremely low. Workers should conduct themselves with the following considerations 
\begin{itemize}
\item  A potential oxygen deprivation hazard due to  exposure to the cover gas. This can be mitigated by ensuring that workers keep their faces well away from open ports to the UI at all times (low risk, low severity)
\item Workers must be aware of pinch points as the purpose of the activity requires sealing heavy metal steel surfaces against each other. (medium risk, low severity)
\item The lids to the motor boxes are heavy, so steps to prevent musculo-skeletal distress should be taken (get help as required and potentially using mechanical assistance if necessary). (medium risk, low severity)
\end{itemize}

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

\section{Procedure}

\subsection{Pre-Requisites}
To conduct this procedure the environment must be prepared. This includes
	\begin{itemize}
	\item The DCR must be well cleaned. This includes vacuuming the floors, wiping down the DCR walls, and wiping down surfaces including shelves and UI
	\item Pass swipe tests on surfaces in the DCR such as the UI, shelving, and URMs.
	\item A benchmark of fewer than 200, 0.5$\mu$m dust counts per $m^{3}$ per second must be achieved in the DCR air.
	\item Prepare all tools for use in a secure location away from the UI, preferably on a trolley for ease of access. This includes wiping down all tools to reduce the chance of dust getting into the UI, ensuring that the required machine screws are available, and wiping down the o-rings.
	\end{itemize}
These cleaning activities and tests must be done on the days prior and the day of the procedure. If at any point the tests fail, cleaning should be redone, and the tests should be done again. 

On the day of the o-ring replacement, the o-rings themselves should have a liberal amount of vacuum grease applied to help them stick in the o-ring grooves during installation.

\subsection{Emergency Procedures}

If there is an all stations call with a side-rope box open
\begin{itemize}
\item Place a cover (the remnants of the North box nitrogen bag should be sufficient) over the open box to provide a dust shield.
\item Change the nitrogen inflow to use a dewar (if using a bottle, switch to using the international). 
\item Maintain the nitrogen flow and monitor it from refuge through the all stations call
\end{itemize}

If there is an all stations call with a side-rope box cover partially in place (i.e. subset of screws installed) or between o-ring replacement procedures. 
\begin{itemize}
\item Change the nitrogen inflow to use a dewar (if using a bottle, switch to using the international). 
\item Maintain the nitrogen flow and monitor it from refuge through the all stations call
\end{itemize}

Assess the situation at the end of the all stations, and determine if work can resume, or if the UI must be put into a safe state (i.e. Cover-gas bags reconnected) until next the working day.

\section{South Load Cell Box Remediation}
\newcounter{southEcounter}
\newcommand\southE{\stepcounter{southEcounter}\thesouthEcounter}
\begin{tabular}{|c|c|p{15cm}|}
\hline\southE & & Remove the cover from the South load cell box by systematically removing the screws from the cover. One or more screws may be stripped, so use the torx bit  or vice grip to extract those cap screws.\\ 
\hline\southE & & Remove the o-rings. The TEV o-rings should be considered single use parts.\\
\hline\southE & & Examine the surface of the flange. The suspicion is that masking tape residue has been left on the load cell box flange based on the earlier attempt and that is responsible for the current leak rate.\\
\hline\southE & & Replace the TEV o-rings with the new load cell box o-rings. There may be some resistance as the o-ring is a tight fit.  \\
\hline\southE & & With one worker holding the box cover, a second worker starts installing the new screws in the cover at the corners. Once the corner screws are started, the cover is eased into place, taking care that the o-ring does not roll or leave their groove. The corner screws tighten should be then be tightened and the remaining screws can be put into place. All the screws should be tightened using a star pattern.\\
\hline\southE & & Check the seal using the helium leak checker.
\begin{itemize}
\item Open one of the inter-o-ring seal VCR ports and connect it to the leak checker (ensuring that the opposing VCR plug is in tact). 
\item Start the leak checker. Once the turbo pump activates (allowing "fine" measurements to be taken) systematically spray each of the edges with helium  looking for the maximum leak rates on each edge. 
\item If a good vacuum cannot be achieved by the leak checker or the leak rate on any particular edge is less that 10$^{-7}$ mbar L/s, stop the leak checker and tighten the screws again. 
\item Repeat as necessary.
\end{itemize}
\vspace{-0.2cm}
\\
\hline
\end{tabular}

\subsection{Procedure time estimates}
For guidance, it is expected that the following procedures will take the following time. 
\begin{itemize}
\item Remove cover screws: 5 minutes
\item Time with direct gas path open to UI: 2-5 minutes to examine, remove, and replace the o-ring, 5-10 minutes to examine and clean the flange, for a total of 7-15 minutes
\item Replace cover screws: 5 minutes
\item Flush the side rope box 30 minutes
\item Leak test the side rope box 30 minutes (can be done at the same time as flushing).
\end{itemize}

\end{document}

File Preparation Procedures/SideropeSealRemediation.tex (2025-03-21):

\documentclass{beamer}

\title{Renewing Motor Box Seals}
\author{Ryan Bayes}

\begin{document}
\frame{\maketitle}

\begin{frame}{Motivation}
\begin{columns}
\column{0.55\textwidth}
\begin{itemize}
\item Know that the UI radon seal is not great
\item Leak rate is significantly reduced through the used of nitrogen bags
	\begin{itemize}
	\item<alert@1> Isolation bag around full UI has produced low radon monitor rates (before pump)
	\item<alert@2> Isolation bags around problematic features reduced rate relative to none
	\end{itemize}
	\end{itemize}
\column{0.5\textwidth}
\includegraphics<1>[width=\textwidth,angle=180]{IMG_4523.jpg}
\includegraphics<2>[width=0.8\textwidth]{UIView.png}
\end{columns}
\begin{itemize}
\item Main sources are;
	\begin{itemize}
	\item North siderope motor box 
	\item East rope extension box
	\end{itemize}
\item Both require o-ring require o-ring replacement
	\begin{itemize}
	\item Reduce nitrogen use by the experiment
	\item Restore functionality of North Motor box (bag cuts off access)
	\end{itemize}
\end{itemize}
\end{frame}

\begin{frame}{Summary of Prior Leak Checking Campaigns}
	\begin{table}
	\begin{tabular}{r|c|c|c}
	Feature & Status & Leak (mbar L/s)& Date\\
	East and west motor box & good & $< 2\times10^{-8}$ & June 2023 \\
	West extension box seal & good & $< 10^{-10}$ & June 2023 \\
	South motor box outer seal & pass & $5\times10^{-7}$ & June 2023 \\
	South motor box inner seal & fail &  $1.4\times10^{-5}$ & July 2023 \\
	South exten. box outer seal & fail &  $< 10^{-5}$ & June 2023 \\
	South exten. box inner seal & pass &  $2\times10^{-9}$ & July 2023 \\
	North motor box & fail &  $ > 10^{-4}$ & Oct 2019 \\
	North exten. box & pass&  $ < 10^{-9}$ & June 2023 \\
	East extension box seal & fail & $ > 10^{-4}$ & Oct 2019 \\
	\end{tabular}
	\end{table}
	\begin{itemize}
	\item CF flanges checked with helium/Argon sniffer
		\begin{itemize}
		\item Neck tube base flanges (Leaks observed and corrected)
		\item Level sensor flanges (no leaks observed)
		\item CF flanges on motor box (motor, electrical feedthroughs; no leaks)
		\end{itemize}
	\item Gloves tested by pumping and purging with N$_{2}$
		\begin{itemize}
		\item East gloves shown to leak, South and West gloves good.
		\end{itemize}
	\end{itemize}
\end{frame}

\begin{frame}{Proposed Intervention}
\begin{columns}
\column{0.65\textwidth}
\begin{itemize}
\item Detector at low voltage
\item Connect N$_{2}$ source to UI to "flush" UI
\item Remove bag from North Motor Box/East Extension Box
\item Remove cover from box
\item Examine/replace O-rings 
\item Replace box cover
\end{itemize}
\column{0.35\textwidth}

\end{columns}
\vspace{-0.5cm}
\begin{block}{Radon mitigation}
\begin{itemize}
\item Keep the UI at positive pressure by adding nitrogen to UI (monitor through DeltaV)
\item Purge air from box after sealing by pulling air from motor box using auxiliary port
	\begin{itemize}
	\item Motor box is 35 L 
	\end{itemize}
\item Restrict air flow path size to less than the 1/2" port available
\end{itemize}
\end{block}

\end{frame}

\begin{frame}{Additional Steps}
	\begin{block}{Inner o-ring on South Motor Box}
		\begin{itemize}
		\item TEV o-ring bad; Viton o-ring "good" but emanates radon
		\item Replacing TEV o-ring could remove radon source
		\end{itemize}
	\end{block}
	\begin{block}{Outer o-ring on South Extension Box}
		\begin{itemize}
		\item TEV o-ring good; Viton bad 
		\item Unknown if this is damage or displacement
		\item TEV o-ring seal requires more torque; can relax with time
		\item Opening the box to inspect/rInn.
		eplace Viton o-ring will improve stability
		\end{itemize}
	\end{block}
\end{frame}

\begin{frame}{Neck Tube Radon Mitigation}
	\begin{columns}
	\column{0.7\textwidth}
	\begin{itemize}
	\item HV feedthroughs are "known" to be radon permiable
		\begin{itemize}
		\item Attempted isolation test but inconclusive
		\item Two isolation bags clearly hold pressure
		\item Two others are not so obvious (but that may be a flow problem)
		\end{itemize}
	\item Seal cannot be improved without completely changing the connection plate
	\item May need another attempt at isolation bags
	\item Increased pressure could improve isolation measure (get that by removing the large bags)
	\item Could improve the material; use aluminized mylar
	\end{itemize}
	\column{0.3\textwidth}
	
	
	
	\end{columns}
	
\end{frame}

\begin{frame}{Summary}
	\begin{itemize}
	\item UI is known to leak radon
		\begin{itemize}
		\item $10^{-4}$ suppression relative to air from UI gas assays
		\item Radon monitor assays give a (much) higher number
		\end{itemize}
	\item Current solution is not sufficient
		\begin{itemize}
		\item Push to complete calibration program makes full UI bag problematic
		\item Current isolation bags interfere with side rope motor box operation
		\item Current bags are not as good as full bag (something is missing)
		\item N$_{2}$ use is restrictive; unclear if we can add further bags and maintain function
		\end{itemize}
	\item Propose to replace radon seals on selected motor box
		\begin{itemize}
		\item North Motor box and East Extension boxes need both o-ring sets replaced
		\item South motor box needs inner o-ring replaced
		\item South extension box needs outer o-ring replaced
		\end{itemize}
	\item Isolation bags on neck tubes should be more efficient without side rope isolation bags
		\begin{itemize}
		\item Some improvements could be considered there
		\end{itemize}
	\end{itemize}
\end{frame}

\end{document}

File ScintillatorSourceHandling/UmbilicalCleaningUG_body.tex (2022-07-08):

\fancyhf{}
% \lhead{\begin{tabular}{|p{8.25cm}} \hline {\large \bf SNO+ Laser Procedures} \\ \\ \\ \\ \end{tabular}}
\lhead{\begin{tabular}{|p{8.25cm}|p{3cm}|p{2.5cm}|p{1.5cm}|}
                \hline
            {\large \bf SNO+ Umbilical Cleaning}
                     & Document No:
                     & Revision No: 01
              %                                                  & Effective Date: 2022-03-21\\
                                                   & Page \thepage \\
\hline
                                                     \end{tabular}}

\begin{tabular}{||l|l|l||}
\hline\hline
& \multicolumn{2}{p{8cm}||}{\bf SNO+ Umbilical Cleaning: Underground} \\
 & \multicolumn{2}{p{8cm}||}{} \\
\hline
\multicolumn{2}{||p{8.5cm}|}{Document Number:} & Revision Number: 01\\
\hline
\multicolumn{3}{||l||}{Document Owner: SNO+ Calibration Post-Doc} \\
\hline
\multicolumn{3}{||l||}{Reviewer:}\\
\hline
Name: & Signature & Date \\
\hline
\multicolumn{3}{||l||}{Authorizer:}\\
\hline
Name: & Signature & Date \\
\hline\hline
\end{tabular}
\thispagestyle{empty}

\newcounter{cbcounter}
\newcommand\showcbcounter{\stepcounter{cbcounter}\thecbcounter}

\section{Requirements}

\begin{itemize}
\item Umbilical underground (containing fibre bundle)
\item Source of LAB (from 60 tonne tanks)
\item Cleaning vessel (aluminum with sealed lid and two nozzles; one terminates to a three way valve with a check valve on one side, second terminate to a standard bellows valve and extends into the cleaning volume through a steel pipe). Must be large enough to contain 30 m of 5/8'' umbilical. Suspect 50 cm diameter, 50 cm tall will be sufficient.
\item Spill kit available during movement of LAB
\item Extra cleaning pads for removing LAB after soaking is complete
\item Gloves must be worn at all times during handling of umbilical and volume
\item Nitrogen source for preparing vessel and to maintain blanket during soaking
\item Radon proof bag to store the umbilica after soaking
\end{itemize}

\section{Procedure}
\subsection{Starting the umbilical soak}
\begin{enumerate}
\item Prepare the cleaning vessel
  \begin{enumerate}
  \item In the chem lab, wipe the vessel inside and out with UPW. 
  \item Connect the lid of the vessel. Purge the vessel with nitrogen.
  \end{enumerate}
\item Open the Umbilical bag and vessel lid. Quickly put the umbilical into the vessel.
\item Close the vessel lid and resume nitrogen purge.
\item Put the vessel on a cart and transport the vessel to the 60 tonne tank area.
\item With two or more people lift the vessel into the 60 tonne tank area and put it in the corner next to the stairs
\item Fill the vessel with LAB through the standard bellows valve (same as the valve used for the nitrogen).
\item Leave room to create a nitrogen blanket within the vessel. Add further nitrogen as necessary. (If necessary create a tent around the lid and fill that with nitrogen).
\item Allow the umbilical to sit for approximately 35 days.
\end{enumerate}  

\subsection{Concluding the umbilical soak}
\begin{enumerate}
\item Connect nitrogen to the three way valve oposite to the checkvalve. Connect the bellows valve to a waste tote via a peristalic pump.
\item Syphon off the LAB while adding nitrogen to keep air from getting into the space. Once the flow stops or becomes intermittant, close the valves to the vessel, stop the pump, and disconnect the syphon line and nitrogen. 
\item Lift the cleaning vessel out of the 60 tonne tank area. Place it on a cart and transport it to the chem lab.
\item Open the vessel. Wipe off residual LAB with cleaning pad while transferring umbilical to radon proof bag. 
\item Fill the bag with nitrogen and seal the bag once transfer is complete.
\item Take umbilical to DCR to wait for installation on URM.
\end{enumerate}

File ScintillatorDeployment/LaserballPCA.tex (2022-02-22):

The Laserball deployment is meant for the purpose of running PMT calibrations (PCA) and optical measurements from within the scintillator. The following steps must be taken to prepare the source for deployment, operate the dye laser, and deploy the source. 

Note that this is only meant to be a rough sketch of the deployment procedure. Some of the details can only be finalized with the hardware tested in place. 

\section{Source Preparation}

\subsection{Connecting the Source to the Umbilical}
If the source is not connected to the umbilical use the following steps to connect the laserball to the umbilical source connector.
\begin{tabular}{|c|p{4cm}|}
\hline
 &  Lock the urm into a maintenance position  \\ \hline
 &  Set the urm cover gas to a purge mode \\ \hline
 &  Open the gate valve at the end of the URM bellows \\ \hline
 &  Lower the connector so that it can be manipulated \\ \hline
 &  Join the laserball to the umbilical with the source connector \\ \hline
 &  Raise the source so that the gate valve can be closed \\ \hline
 &  Continue purging the urm while monitoring radon levels. If using a Rad7 to monitor the levels the reading must be consistent with zero. The purging must be monitored by an operator while running. The radon levels must meet specification before further activity can occur. If the radon levels do not meet specification put the URM cover gas system in standby mode and resume purging in a subsequent shift. \\ \hline
 \end{tabular}
 
 \subsection{Using the Source Cleaning Vessel}
 The source cleaning vessel must be used prior to deployment to ensure an absence of particulates on the source surface that may contaminate the scintillator in the acrylic vessel. The steps required are as follows;
 \begin{tabular}{|c|p{4cm}|}
 \hline
& Position the genie lift so that the forks will pass through the source cleaning vessel frame lifting points. \\ \hline
& Raise the cleaning vessel frame just enough so that it can be transported to the URM gate valve. \\ \hline
& Check the height of the URM gate valve. If the gate valve is below the SCV flange the position of the gate valve must be adjusted by shortening the length of the turnbuckles supporting the URM gate valve. \\ \hline
& Position the cleaning vessel underneath the URM with the Genie lift wheels parallel to the URM axis. This ensures consistency in the clocking of the flange. \\ \hline
& Lift the SCV up to the URM gate valve. When the SCV is close to the gate valve, start threading the bolts connecting the SCV to the gate valve from underneath. Continue lifting the SCV to the gate valve until the surfaces are in contact. Tighten the bolts to hand tight, then apply no more than a quarter turn on each bolt with a wrench in a star pattern to apply equal force across the flange. Raise the genie lift as much as possible to take the weight of the SCV off of the URM.\\ \hline
& Flush nitrogen through the source cleaning vessel \\ \hline
&  Set the urm to purge mode and open the gate valve. \\ \hline
& Turn on the spray system and lower and raise the source through the spray jets (might program a macro into manip to automate this). \\ \hline
& Repeated lab samples from the cleaning should be subjected to QA to evaluate contamination over time. Raise the source above the gate valve once criteria is reached (criteria to be established).  \\ \hline
& Remove the source cleaning vessel from the urm gate valve by first removing the bolts, lowering the source cleaning vessel on the genie lift, and then removing the source cleaning vessel from underneath the URM. \\ \hline 
  \end{tabular}
  
\section{Calibration Deployment Procedures}

\subsection{Preparation for Deployment}
The following steps must be done before the source deployment. If there is a problem noted here then it is expected that the calibration operation will stop until the problem is resolved with the approval of the site activities coordinator and the calibration expert. 
\begin{tabular}{|c|p{4cm}|}
& Measure the height of the ui relative to the Ibeam. Ensure that the ui height will allow for the source to be used (specification needed). This height must be entered into manip (formula to be added). \\ \hline
& With the laser disconnected from the umbilical, start the nitrogen/dye laser. Select the required dye for the desired first wavelength and set the neutral density filters to block the light. Connect the umbilical to the laser. \\ \hline
& Unlock the urm from maintenance position and move the urm to mate with the ui gate valve. Clamp the urm over the ui \\ \hline
& Connect the urm gate valve to the nipple assembly above the ui gate valve (details to come). \\ \hline
& Pump and purge the space between the gate valves using the nipple assembly. \\ \hline
& While monitoring the pressure in the urm open the urm gate valve to the nipple assembly space. Ensure that the cover gas bag is half inflated (not flat or too full indicating an over or under pressure state). Add or remove nitrogen if needed. \\ \hline
\end{tabular}

\subsection{Deploying the Source}
This is the point of no return for the calibration requiring the approval of the site activities coordinator and the calibration expert. 
\begin{tabular}{|c|p{4cm}|}
& With the knowledge and approval of the shifter, cover gas, and AV operators carefully open the ui gate valve. \\ \hline
& With the approval of the cover gas and AV operators, slowly and carefully lower the source into the AV. Monitor the rope and umbilical tensions for changes suggesting that the source meets the lab surface.\\ \hline
& If using the side ropes lower the source until  it can be reached by the gloves ($\approx$1350 cm). Follow steps to mount the side ropes onto the source carriage. \\ \hline
&  Lower the source in steps until it is immersed in lab. Then the source can be lowered to the centre of the detector. \\ \hline
& Assuming the laser is already running with the neural density filters set to block the light; open the neural density filters to produce the desired intensity per pulse (monitored with EXTA nhits). For a PCA this is between 100 and 200 nhits per pulse. \\ \hline
& Follow the run plan
  \begin{enumerate}
	\item For a PCA; 1-2 hours in the centre of the detector such that there are more than 10000 hits per pmt on average. 
	\item For a scan; 15-20 minutes at each location other than the central PCA run. Further details to be set by the run plan. 
  \end{enumerate} \\ \hline
& When finished; retract the source  with stop points at 1200, 1250, 1300, 1350. Remove the side ropes if necessary. Continue retracting the source in steps reducing in size until the source reaches the reference point. \\ \hline
& With the knowledge and approval of the covergas operator, carefully close the ui gate valve. \\ \hline
& Check the position of the source pivot through the source tube viewport. Ensure that the pivot is where it is expected to be. \\ \hline
& Close the urm gate valve. Drain lab from urm. \\ \hline
\end{tabular}

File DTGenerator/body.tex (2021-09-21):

\fancyhf{}
% \lhead{\begin{tabular}{|p{8.25cm}} \hline {\large \bf SNO+ Laser Procedures} \\ \\ \\ \\ \end{tabular}}
\lhead{\begin{tabular}{|p{8.25cm}|p{6cm}|}  
	\hline 
		{\large \bf SNO+ DT Generator Procedures}  
										& Document No:  \\ 
								\cline{2-2} & Revision No: 02\\  
								\cline{2-2} & Effective Date: 2017-08-08\\ 
								\cline{2-2} & Page \thepage \\  \end{tabular}}

\begin{tabular}{||l|l|l||}
\hline\hline
& \multicolumn{2}{p{8cm}||}{\bf SNO+ DT Generator Procedures} \\
 & \multicolumn{2}{p{8cm}||}{} \\
\hline
\multicolumn{2}{||p{8.5cm}|}{Document Number:} & Revision Number: 02\\
\hline
\multicolumn{3}{||l||}{Document Owner: SNO+ Calibration Post-Doc} \\
\hline
\multicolumn{3}{||l||}{Reviewer:}\\
\hline
Name: & Signature & Date \\
\hline
\multicolumn{3}{||l||}{Authorizer:}\\
\hline
Name: & Signature & Date \\
\hline\hline
\end{tabular}
\thispagestyle{empty}

\section{Purpose}

The following procedures describe the operation of the N16 calibration source, and the DT generator. 

\section{Summary of Procedures}

The following procedures are contained in this document.

\begin{itemize}
\item DT generator emergency shutdown procedures
\item DT generator turn on procedure
\item DT generator turn off procedure
\item Gas board startup procedure
\item Adjusting the neutron generator target position
\item N16 source startup procedure
\item N16 source shutdown procedure
\item N16 PMT turn on procedure
\item N16 PMT turn off procedure
\item DT pit disassembly procedure \\ \\ \\ \\ \\ \\
\item DT pit assembly procedure 
\item NCD counter calibration procedure
\end{itemize} 

\section{Definitions}

\section{Procedures}

\subsection{ DT generator emergency shutdown procedures}

This procedure describes how to turn off the DT generator and gas board in case of an emergency such as fire, severe gas leak, radiation problem etc.
\begin{enumerate}
\item \CheckBox[name=dtesp1]{} {\bf Turn off HV.}
\item \CheckBox[name=dtesp2]{} Turn off neutron pulser.
\item \CheckBox[name=dtesp3]{} Turn key to "Off".
\item \CheckBox[name=dtesp4]{} Close main valve on CO$_2$ bottle.
\end{enumerate}

\pagebreak
\subsection{ DT generator turn on procedure}

This procedure describes how to turn on the DT generator prior to operating eith the N16 of LI8 sources. Only authorized DT operator are allowed to operate the generator.
\subsubsection{Prior To This Procedure}
\begin{itemize}
\item \CheckBox[name=dttop01]{} DT generator is off
\end{itemize}
\subsubsection{Summary of Procedure}
\begin{itemize}
\item \CheckBox[name=dttop02]{} {\bf Make sure you understand the DT Generator shutdown and emergency shutdown procedures.}
\item \CheckBox[name=dttop03]{} Secure DT generator area.
\item \CheckBox[name=dttop04]{} Turn on spare NCD counter.
\item \CheckBox[name=dttop05]{} Check operation of DT generator at full NOC setting.
\item \CheckBox[name=dttop06]{} Record maximum and minimum neutron flux.
\end{itemize}

\begin{tabular}{|l|l|}
\hline
\multicolumn{2}{|l|}{} \\
\multicolumn{2}{|l|}{\bf DT Generator Turn On Procedure} \\
\multicolumn{2}{|l|}{} \\
\hline
& \\
\TextField[name=dttopop,backgroundcolor=0.975 0.975 0.975,width=2cm]{Operator: } &
\TextField[name=dttopd,backgroundcolor=0.975 0.975 0.975,width=4cm]{Date: } \\
& \\
\hline
\end{tabular}
\begin{enumerate}
\item \CheckBox[name=dttop1]{} Read and make sure you {\bf understand} the DT Generator Turn Off procedures (also referred to as the DT Generator Shutdown procedures).
% \item \CheckBox[name=dttop2]{} If it is not already on, turn on the gas computer. \\ {\it The use of the gas computer is optional.}
% \item \CheckBox[name=dttop3]{} If it is not already running, start the Gas/DT monitoring program on the gas computer by:
%	\begin{enumerate}
%	\item start labview from the programs menu.
%	\item from the labview file menu item select \verb+open+.
%	\item go to \verb+c:/labview/develop/+.
%	\item select \verb+febain.vi+.
%	\item After the VI has loaded click on the run (arrow) button.
%	\end{enumerate}
%\item \CheckBox[name=dttop4]{} If it is not already running and selected, on the labview monitoring program, click on the {\bf fraser monitor} check box.
\item \CheckBox[name=dttop5]{} Secure the DT area: ensure that the shielding blocks (the "donuts") are in place and that the grey interlock boxes are in place and connected.
\item \CheckBox[name=dttop6]{} Turn on the main instrument panel, the flow controller and the stepper motor controller.
\item \CheckBox[name=dttop7]{} Set the Interlock Override on the main instrument panel to "On" for manual control (normal setting).
\item \CheckBox[name=dttop8]{} Check the high Voltage (HV) and neutron pulser switches on the DT control panel are in the OFF position.
\item \CheckBox[name=dttop9]{} Set the Neutron Pulse Control (NPC) to 5 and the Neutron Output Control (NOC) to 0.
\item \CheckBox[name=dttop10]{} Make sure the HV supply for the space NCD counter is turned off and the dial setting is at 0.
\item \CheckBox[name=dttop11]{} Turn on the NIM bin with the Fast Neutrino Flux Meter (F.N.F.M.).
\item \CheckBox[name=dttop12]{} Turn on the low voltage power supply for the NCD counter.
\item \CheckBox[name=dttop13]{} Turn on the F.N.F.M high voltage supply and set the voltage to 800 V.
\item \CheckBox[name=dttop14]{} (Optional) Connect an oscilloscope to the spare NCD counter amplifier. Set timebase to approximately 1 $\mu$s/div and vertical scale to a small fraction of a volt per division.
\item \CheckBox[name=dttop15]{} Turn on the HV for the space NCD counter. While watching the scope fro pulses slowly (about 1 minute) increase the voltage to 1850 V.
\item \CheckBox[name=dttop16]{} (Optional) Connect an oscilloscope to the SYNC output. Set timebase to approximately 2 ms full sweep.
\item \CheckBox[name=dttop17]{} Insert the DT generator key and turn on the power.
\item \CheckBox[name=dttop18]{} At this time, the main power light on the DT control panel, and the {\bf D.T. GEN ON} light located behind the DT Pit should be on. {\bf if either of these lights do not come on, proceed to step five in the shutdown procedure.} {\it The interlock system has many inputs any of which can cause the controller not to operate. One set of inputs come from the water sensors. There are currently 4 separate water sensors (3 in the DT pot and one in the sump). In addition the concrete blocks have to be in place (and wired) and there is a computer controlled input. Troubleshooting of this system is beyond the scope of this document.}
\item \CheckBox[name=dttop19]{} Switch the neutron pulser on. Make sure that the neutron pulser light comes on. {\bf If the neutron pulser light does not come on, proceed to step number four of the shutdown procedure immediately.}
\item \CheckBox[name=dttop21]{} Verify that the DT generator is pulsing at 1.8 ms and that the pulse width is 180~$\mu$s.
\item \CheckBox[name=dttop22]{} Leave the pulser running for approximately one minute.
\item \CheckBox[name=dttop23]{} When the HV is turned on the "normal" (green) adn the "high current" (red) will likely flicker for a few seconds after which the green light will be off for a while before it comes on steady. The red light should be off. {\bf There is now a built in timedelay in the DT generator source circuit --- it may take up to 1 minute for the green light to be steady. As long as the red light does not come on don't panic. If the green light continues to flicker past 20 seconds or the red light comes on steady proceed immediately to the shutdown procedure.}
\item \CheckBox[name=dttop24]{} Record the high voltage turn on time below, as well as in the DT Generator Log Book.
\begin{center}
\begin{tabular}{|c|}
\hline
\\
\TextField[name=dttopop,backgroundcolor=0.975 0.975 0.975,width=3cm]{HV Turn on Time:} \\
\\
\hline
\end{tabular}
\end{center}
\item \CheckBox[name=dttop25]{} Record initial value of the F.N.F. Meter,
\begin{center}
\begin{tabular}{|c|}
\hline
\\
\TextField[name=dttopfng,backgroundcolor=0.975 0.975 0.975,width=3cm]{FNFM Gauge Reading:} \\
\\
\hline
\\
\TextField[name=dttopfnc,backgroundcolor=0.975 0.975 0.975,width=3cm]{FNFM Computer Reading:} \\
\\
\hline
\end{tabular}
\end{center}
{\it The F.N.F.M. should read approximately 0.5$\times 10^{3}$ at minimum and $\approx 4\times 10^{3}$ at full NOC setting. If it deviates by more than 30\% {\bf immediately} proceed to the shutdown procedure and contact the OCE.}
\item \CheckBox[name=dttop26]{} Increase the NOC to 10 (slowly over a period of 20 seconds).
\item \CheckBox[name=dttop27]{} Record the final (max) value of the F.N.F. Meter,
\begin{center}
\begin{tabular}{|c|}
\hline
\\
\TextField[name=dttopfng,backgroundcolor=0.975 0.975 0.975,width=3cm]{FNFM Gauge Reading:} \\
\\
\hline
\\
\TextField[name=dttopfnc,backgroundcolor=0.975 0.975 0.975,width=3cm]{FNFM Computer Reading:} \\
\\
\hline
\end{tabular}
\end{center}
\item \CheckBox[name=dttop28]{} Reset the NCD counter scaler.
\item \CheckBox[name=dttop29]{} The NCD counter should be counting at 17-18 Hz at maximum NOC rate and about 3 Hz at miniumum NOC rate. If the rate differs by more than 30\% immediately proceed to the shutdown procedure and contact the OCE.
\item \CheckBox[name=dttop30]{} Record the start time and the initial flux on the DT Generator Log Sheet.
\item \CheckBox[name=dttop31]{} Turn the NOC setting back down to zero until the source is deployed.
\end{enumerate}

\pagebreak
\subsection{ DT generator turn off procedure}

This procedure describes how to turn off the DT generator. A trained and authorized DT generator operator is required to perform this procedure except {\bf in an emergency}.

\begin{tabular}{|c|c|}
\hline
\multicolumn{2}{|l|}{} \\
\multicolumn{2}{|l|}{\bf DT Generator Turn Off Procedure} \\
\multicolumn{2}{|l|}{} \\
\hline
& \\
\TextField[name=dttfop,backgroundcolor=0.975 0.975 0.975,width=2cm]{Operator: } &
\TextField[name=dttfd,backgroundcolor=0.975 0.975 0.975,width=4cm]{Date: } \\
& \\
\hline
\end{tabular}
\begin{enumerate}
\item \CheckBox[name=dttfp1]{} Decrease the NOC from 10 to 0 (Slowly over a period of 20 sec.) Leave the Neutron Pulse Control at 5.
\item \CheckBox[name=dttfp2]{} Turn the HV Off. Record this time in the DT Logbook.
\begin{center}
\begin{tabular}{|c|}
\hline
\\
\TextField[name=dttft,backgroundcolor=0.975 0.975 0.975,width=4cm]{HV Turn off Time: }\\
\\
\hline
\end{tabular}
\end{center}
\item \CheckBox[name=dttfp3]{} Wait 1 minute.
\item \CheckBox[name=dttfp4]{} Switch the neutron pulser off.
\item \CheckBox[name=dttfp5]{} Turn the DT Generator off and return keys to their proper location in the $^{16}$N cabinet.
\item \CheckBox[name=dttfp6]{} Record the NCD counter total:
\begin{center}
\begin{tabular}{|c|}
\hline
\\
\TextField[name=dttfd,backgroundcolor=0.975 0.975 0.975,width=4cm]{Dose:}\\
\\
\hline
\end{tabular}
\end{center}
\item \CheckBox[name=dttfp7]{} Turn down the HV for the NCD counter (slowly!).
\item \CheckBox[name=dttfp8]{} Turn off the NV for the NCD counter.
\item \CheckBox[name=dttfp9]{} Turn off the low voltage powersupply for the NCD counter.
\item \CheckBox[name=dttfp10]{} Turn off HV for FNFM (just turn it off, don't ramp down).
\item \CheckBox[name=dttfp11]{} Turn off the NIM bin.
\item \CheckBox[name=dttfp12]{} Fill out the DT Generator Log Sheet.
\end{enumerate}
\pagebreak
\begin{center}
{\bf DT Generator Log Sheet}
\end{center}
\pagebreak
\begin{tabular}{|c|}
\hline
\\
\TextField[name=dtlspm,backgroundcolor=0.975 0.975 0.975,width=4cm]{Previous Total Minutes:}\\
\\
\TextField[name=dtlsph,backgroundcolor=0.975 0.975 0.975,width=4cm]{Previous Total Hours:}\\
\\
\hline
\end{tabular}

\begin{tabular}{|c|c|c|c|c|c|c|c|c|c|}
\hline
\multicolumn{3}{|c|}{start} & & \multicolumn{4}{c|}{stop} & duration & total \\
\hline
yy/mm/dd & hh:mm & FNFM & operator & yy/mm/dd & hh:mm & FNFM & NCD counter & time & total \\
 & & (hz) & & & (hz) & counts & (min) & minutes & \\
\hline
&&&&&&&&& \\ \hline 
&&&&&&&&& \\ \hline 
&&&&&&&&& \\ \hline 
&&&&&&&&& \\ \hline 
&&&&&&&&& \\ \hline 
&&&&&&&&& \\ \hline 
&&&&&&&&& \\ \hline 
&&&&&&&&& \\ \hline 
&&&&&&&&& \\ \hline 
&&&&&&&&& \\ \hline 
&&&&&&&&& \\ \hline 
&&&&&&&&& \\ \hline 
&&&&&&&&& \\ \hline 
&&&&&&&&& \\ \hline 
&&&&&&&&& \\ \hline 
&&&&&&&&& \\ \hline 
&&&&&&&&& \\ \hline 
&&&&&&&&& \\ \hline 
&&&&&&&&& \\ \hline 
&&&&&&&&& \\ \hline 
&&&&&&&&& \\ \hline 
&&&&&&&&& \\ \hline 
&&&&&&&&& \\ \hline 
&&&&&&&&& \\ \hline 
&&&&&&&&& \\ \hline 
&&&&&&&&& \\ \hline 
&&&&&&&&& \\ \hline 
&&&&&&&&& \\ \hline 
&&&&&&&&& \\ \hline 
&&&&&&&&& \\ \hline 
&&&&&&&&& \\ \hline 
&&&&&&&&& \\ \hline 
\end{tabular}

\begin{tabular}{|c|}
\hline
\\
\TextField[name=dtlsm,backgroundcolor=0.975 0.975 0.975,width=4cm]{Total Minutes:}\\
\\
\TextField[name=dtlsh,backgroundcolor=0.975 0.975 0.975,width=4cm]{Total Hours:}\\
\\
\hline
\end{tabular}

\pagebreak

\subsection{ Gas board startup procedure}
\begin{tabular}{|c|c|}
\hline
& \\
\TextField[name=dttfop,backgroundcolor=0.975 0.975 0.975,width=2cm]{Operator: } &
\TextField[name=dttfd,backgroundcolor=0.975 0.975 0.975,width=4cm]{Date: } \\
& \\
\hline
\end{tabular}

\begin{figure}
	\begin{center}
	
	\end{center}
	\caption{N16 Gas Panel}
	\label{fig:n16gaspanel}
\end{figure}

\begin{enumerate}
\item \CheckBox[name=gbsp1]{} Verify all valves on the gas board are closed.
\item \CheckBox[name=gbsp2]{} Verify the N$_{2}$/CO$_{2}$ flow control (side B) is off (fully CCW).
\item \CheckBox[name=gbsp3]{} Verify the Solenoid Valve II switch is in the OFF position.
\item \CheckBox[name=gbsp4]{} Enter the DCR using standard entry procedure and verify that
\begin{itemize}
\item \CheckBox[name=gbsp4a]{} the gas input line is connected to the "dry" end of the umbilical
\item \CheckBox[name=gbsp4b]{} the "blue" valve is in the open position
\item \CheckBox[name=gbsp4c]{} the gas return line is connected to the "dry" end of the umbilical 
%\item \CheckBox[name=gbsp4d]{} the pressure transducer is powered up and that a voltmeter is connected to it.
%\item \CheckBox[name=gbsp4e]{} the voltmeter is reading the correct (18 psi) "pressure".
\end{itemize}
%{\it The pressure transducer is hooked up in a temporary way for the time being. Consult the OCE for details.}
\item \CheckBox[name=gbsp5]{} Turn on the power on the main instrument panel and the dual flow controller box.
\item \CheckBox[name=gbsp6]{} Flip the switch on flow controller box to "B" (for N$_{2}$ and/or CO$_{2}$). The reading takes a few minutes to equilibrate to zero or near zero.
\item \CheckBox[name=gbsp7]{} Ensure that the C)$_{2}$ bottle is hooked up to the input line at valve VA2.
\item \CheckBox[name=gbsp8]{} Check that VA2 is closed.
\item \CheckBox[name=gbsp9]{} Close the needle valve on the CO$_2$ bottle.
\item \CheckBox[name=gbsp10]{} Open the main CO$_2$ bottle valve.
\item \CheckBox[name=gbsp11]{} Set the regulator to 80 PSIG. note that once the gas starts flowing the regulator and bottle starts to cool off and you sill have to readjust the setting.
\item \CheckBox[name=gbsp12]{} Record the bottle pressure:
\begin{center}
\begin{tabular}{|c|c|}
\hline
Transducer & Reading \\
\hline
CO$_{2}$ Bottle Pressure & \\
(PSIG) & \\
\hline
\end{tabular}
\end{center}
{\it The pressure of a full bottle is 850 to 900 psi G. The CO$_{2}$
in the bottle is in liquid or solid form and the pressure will stay
relatively high until gas only and will drop rapidly thereafter.}%  The CO$_{2}$ regulator has a small white plastic insert (disc with samll hole) in order to seal to the bottle. Don't damage or lose it.}
\item \CheckBox[name=gbsp13]{} Open the inline needle valve after the CO$_2$ regulator.
\item \CheckBox[name=gbsp14]{} Open SVII by setting the switch on the main control panel to {\bf MAN}.
\item \CheckBox[name=gbsp15]{} Open the manual shut-off valve VB2.
\item \CheckBox[name=gbsp16]{} Direct flow to the CO$_2$/N$_2$ flow meter using valve VC1.
\item \CheckBox[name=gbsp17]{} Set the CO$_2$/N$_2$ flow meter to manual and turn the control knob on turn so that some gas will flow.
\item \CheckBox[name=gbsp18]{} Direct flow towards the CO$_2$/N$_2$ flow meter using valve VD1.
\item \CheckBox[name=gbsp19]{} Direct flow to the N16 target chamber using valve VF1. Make sure you are not sending it to the oven!
\item \CheckBox[name=gbsp20]{} Open valve VF2 to accept the returning CO$_2$.
\item \CheckBox[name=gbsp21]{} Open valve VC2.
\item \CheckBox[name=gbsp22]{} Direct the flow towards the exhaust using valve VB4.
\item \CheckBox[name=gbsp23]{} Open the exhast needle valve VA4 fully.
\item \CheckBox[name=gbsp24]{} {\bf Slowly} open valve VA2 and look to see if gas is flowing.
\item \CheckBox[name=gbsp25]{} {\bf Slowly} increase the flow until you reach around a 200-280 reading. Make sure P1 never goes above 100 PSIA. Remember that the time constants are long.
\item \CheckBox[name=gbsp26]{} Record Gas Pressure and Flow.
\begin{center}
\begin{tabular}{|c|c|}
\hline
Transducer & Reading \\
\hline
P1 & \\
(PSIA) & \\
\hline
P2 & \\
(PSIA) & \\
\hline
P3 & \\
(PSIA) & \\
\hline
P4 & \\
(PSIA) & \\
\hline
Flow & \\
(cc/s x (1/1000)) & \\
\hline
Target & \\
Position & \\
\hline
\end{tabular}
\end{center}
\item \CheckBox[name=gbsp27]{} Go back to the DCR and verify that the pressure in the N16 source chamber is within the acceptable upper limit. {\it This is done by checking the voltage reading from the pressure transducer. The transducer gets its power from the monitor PMT supply. Contact the OCE for details.}
\end{enumerate}
\pagebreak

\subsection{ Adjusting the neutron generator target position}

This procedure describes how to change the position of the neutron generator target ladder position. This procedure is used to move from the N16 target to the Li8 target or to adjust the neutron capture efficiency on a target (for example if it is desired to decrease the N16 rate). The nominal target positions for the N16 and Li8 are listed in table \ref{tab:ngenpos}
\begin{table}
\begin{center}
\begin{tabular}{|c|c|}
\hline
Target & Position \\
\hline
N16 & 36.4 \\
Li8 & 101 \\
\hline
\end{tabular}
\caption{Neutron Generator Target Positions}
\end{center}
\label{tab:ngenpos}
\end{table}

{\bf Procedure}

\begin{center}
\begin{tabular}{|c|c|p{7cm}|l|}
\hline
\multicolumn{4}{|l|}{Adjusting Neutron Generator Target Position}\\
\hline
& & & \\
Date & Initial & Procedure & Data and Comments \\
& & & \\
\hline
& & & \\
& & Turn on Power & \\
& & & \\
\hline
& & & \\
& & Run switch in down position & \\
& & & \\
\hline
& & & \\
& & Stop switch in down position & \\
& & & \\
\hline
& & & \\
& & in1 in up position & \\
& & & \\
\hline
& & & \\
& & in2 in up position & \\
& & & \\
\hline
& & & \\
& & in3 in up position & \\
& & & \\
\hline
& & & \\
& & speed set to HIGH & \\
& & & \\
\hline
& & & \\
& & Use jog forward/reverse to change position to desired position & \\
& & & \\
\hline
& & & \\
& & Turn off controller box & \\
& & & \\
\hline
\end{tabular}
\end{center}

\subsection{ N16 PMT turn on procedure}

This procedure describes how to turn on the N16 monitoring PMT.

\begin{enumerate}
\item \CheckBox[name=n16pmt1]{} Verify that the HV controller is turned off and that the dial is turned fully CCW.
\item \CheckBox[name=n16pmt2]{} Verify that the controller cable is plugged into the HV controller.
\item \CheckBox[name=n16pmt3]{} Verify that the controller cable is connected to the "dry" end of the umbilical.
\item \CheckBox[name=n16pmt4]{} Connect a fast oscilloscope to the linear PMT output at the "dry" end of the umbilical. Terminate with a (real) 50 $\Omega$ resistor.
\item \CheckBox[name=n16pmt5]{} Set scope to something link 10 mV per division vertical, 10-20 ns per division horizontal, trigger on negative edge. Use AUTO trigger at first to verify presence of baseline/noise.
\item \CheckBox[name=n16pmt6]{} Turn on the NIM bin.
\item \CheckBox[name=n16pmt7]{} Turn on HV switch.
\item \CheckBox[name=n16pmt8]{} Start dialling (slowly!) up the HV while watching the scope. You should see the glitches and changes in baseline on the scope as you do so. If not stop immediately and check the scope is setup correctly.
\item \CheckBox[name=n16pmt9]{} Real PMT signals should be evident at a voltage setting at of above 2.00.
\item \CheckBox[name=n16pmt10]{} Slowly increase the setting to 2.37 while watching for signs of breakdown. If you see any {\bf stop immediately} and reduce the voltage. Contact the OCE. {\it There may be a tag attached to the power supply with a different voltage than the one listed above. Always use the value on the tag if there is one.}
\item \CheckBox[name=n16pmt11]{} Disconnect the scope.\\ The next steps need only be done if this procedure is executed as part of a general N16 procedure.
\item \CheckBox[name=n16pmt12]{} Verify that the FECD input at 17/15/4
  is disconnected. Leave the ''tee'' and 50 $\Omega$ terminator in place.
\item \CheckBox[name=n16pmt13]{} Use the N16 custom cable to connect the N16 PMT to the correct spigot near the door. Cable tie this cable to the URM. Don't cable tie to the "dry" end part of the N16 cable! \\ {\it It is important that this cable be a short as possible to get the correct trigger timing. Don't just use any random cable you find. Use the correct cable. Also the "dry" end of the N16 PMT cable is fragile. Do {\bf not} cable tie to it. Cable tie to the long cable instead.}
\item \CheckBox[name=n16pmt14]{} Do not connect 17/15/4 until permission has been obtained from the detector operator.
\end{enumerate}

\subsection{ N16 PMT turn off procedure}

This procedure describes how to turn off the N16 monitoring PMT.
\begin{enumerate}
\item \CheckBox[name=n16pof1]{} Disconnect the cable at 17/15/4. Leave
  the "tee" and the 50 $\Omega$ terminator in place.
\item \CheckBox[name=n16pof2]{} Disconnect the cable going from the "dry" end to the patch panel near the door. Coil it up and hang it on the cable rack.
\item \CheckBox[name=n16pof3]{} Turn down (slowly!) the HV control to a dial setting of zero.
\item \CheckBox[name=n16pof4]{} Turn off the HV supply.
\item \CheckBox[name=n16pof5]{} Turn off the NIM bin.\\ {\it This also turns off the power to the pressure transducer. You may have to delay the last two steps until a later time.}
\end{enumerate}

\pagebreak
\subsection{ N16 source startup procedure}

This procedure describes how to turn on the N16 source. An authorized DT and N16 operator is required to perform this procedure.

{\bf State Prior To This Procedure}
\begin{itemize}
\item \CheckBox[name=sspp1]{} DT generator is OFF.
\item \CheckBox[name=sspp2]{} Gas flow to N16 gas board and chamber is OFF.
\item \CheckBox[name=sspp3]{} N16 chamber is assembled and connected to gas board.
\end{itemize}

{\bf Summary of Procedure}
\begin{itemize}
\item \CheckBox[name=sopn161]{} Turn on DT generator.
\item \CheckBox[name=sopn162]{} Set up the N16 gas board.
\item \CheckBox[name=sopn163]{} Turn on the CO$_2$ gas flow to the gas board.
\item \CheckBox[name=sopn164]{} Adjust to desired flow rate.
\item \CheckBox[name=sopn165]{} Check pressure in N16 source chamber.
\item \CheckBox[name=sopn166]{} Turn on N16 PMT.
\item \CheckBox[name=sopn167]{} Adjust NOC and target position to desired $^{16}$N rate.
\end{itemize}

\begin{tabular}{|c|c|}
\hline
\multicolumn{2}{|l|}{}\\
\multicolumn{2}{|l|}{\bf N16 Source Startup Procedure}\\
\multicolumn{2}{|l|}{}\\
\hline
& \\
\TextField[name=dttfop,backgroundcolor=0.975 0.975 0.975,width=2cm]{Operator: } &
\TextField[name=dttfd,backgroundcolor=0.975 0.975 0.975,width=4cm]{Date: } \\
& \\
\hline
\end{tabular}
\begin{itemize}
\item \CheckBox[name=n16p1]{} Complete DT Generator startup procedure.
\item \CheckBox[name=n16p2]{} Complete Gas Board startup procedure.
\item \CheckBox[name=n16p3]{} Complete N16 PMT Turn On procedure.
\item \CheckBox[name=n16p4]{} Complete $^{16}$Detector Setup procedure.
\end{itemize}
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

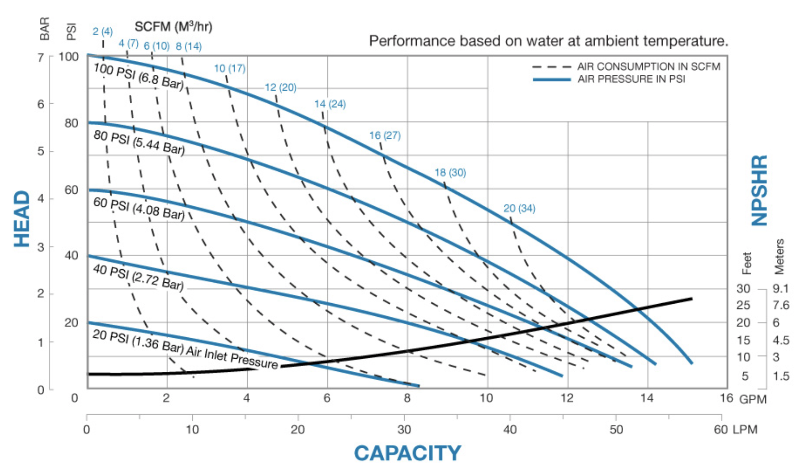
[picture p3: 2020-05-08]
figures/curve.png

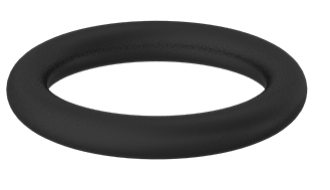
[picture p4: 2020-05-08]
figures/oring.png

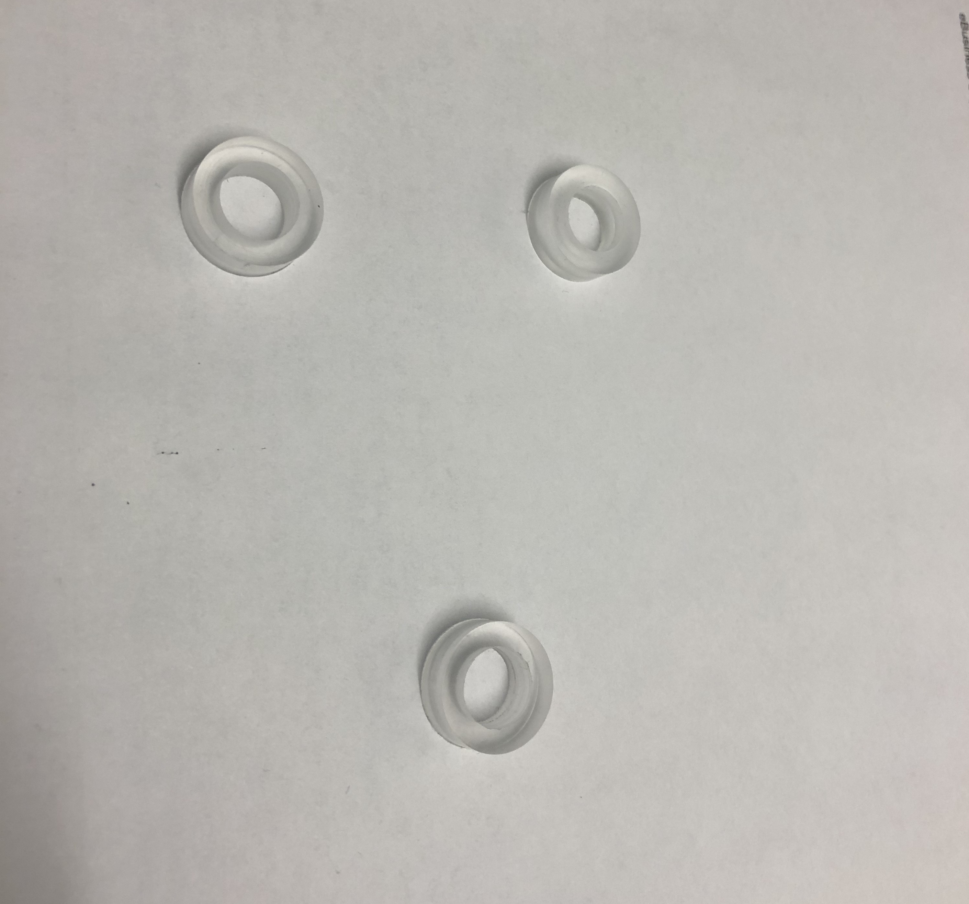
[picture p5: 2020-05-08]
figures/plug1.jpg

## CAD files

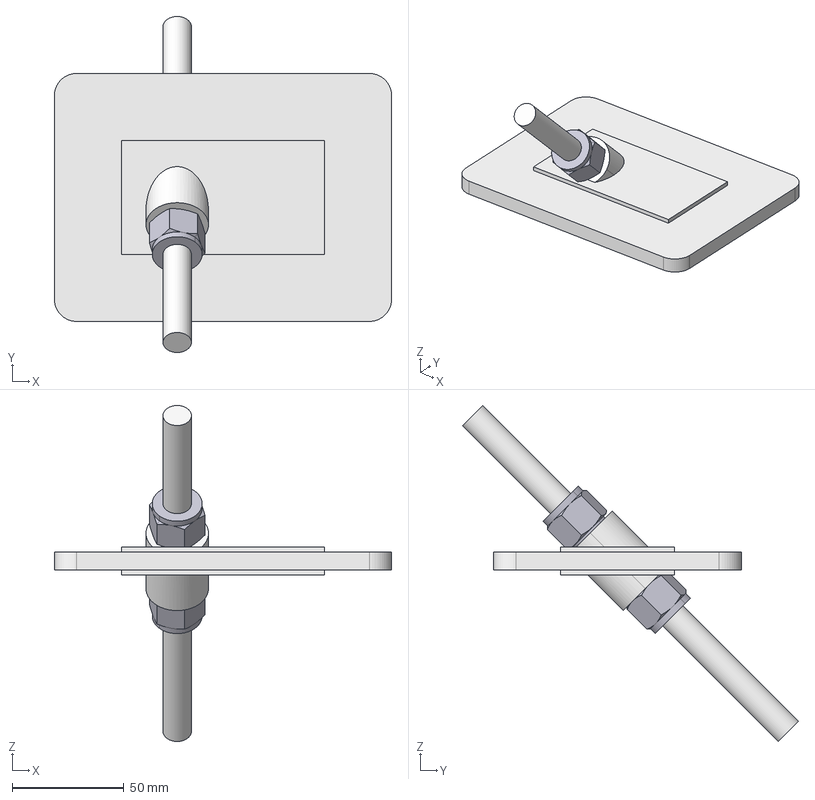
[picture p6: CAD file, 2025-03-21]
Preparation Procedures/UmbilicalFeedthroughPlateMockup.FCStd
151.0 x 150.4 x 150.4 mm

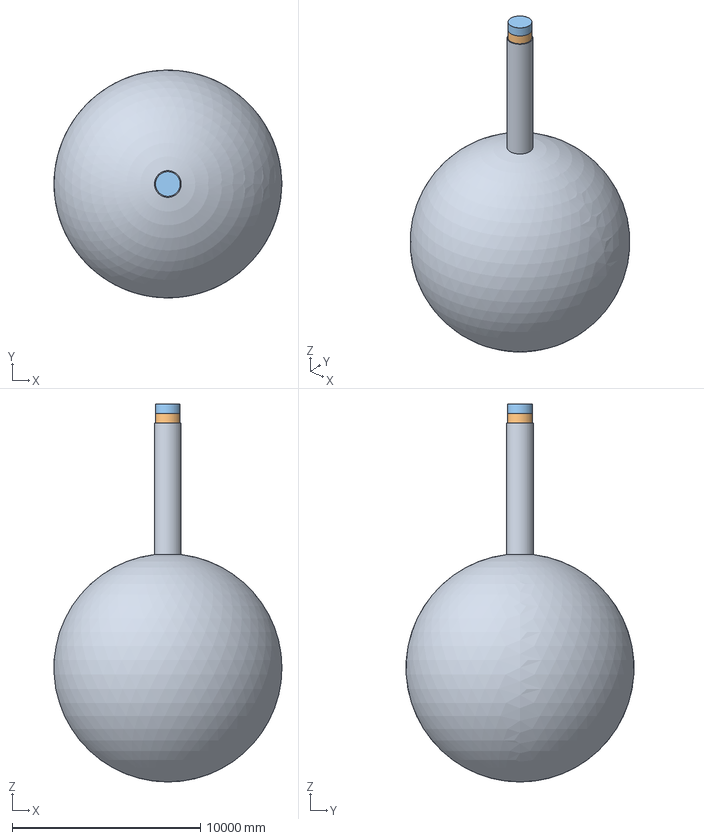
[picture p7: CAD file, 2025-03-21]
Preparation Procedures/SNO+Mockup.FCStd
12106.3 x 12092.9 x 20073.0 mm
Tube001

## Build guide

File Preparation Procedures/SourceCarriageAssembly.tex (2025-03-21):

\documentclass[12pt]{article}
\usepackage{subcaption}
\usepackage{graphicx}

\usepackage{pifont,amssymb} % for the symbols
\usepackage[shortlabels]{enumitem}

\newlist{answerlist}{enumerate}{2}
\setlist[answerlist]{label={\arabic*.\makebox[0pt][r]{\noexpand\emptysquare\hspace{2em}}},ref=\alph*}

\newcommand{\emptysquare}{$\square$}
\newcommand{\checkedsquare}{\makebox[0pt][l]{\raisebox{1pt}[0pt][0pt]{\large\hspace{1pt}\cmark}}$\square$}
\newcommand{\cmark}{\ding{51}}%
\newcommand{\correctanswer}{{\renewcommand{\emptysquare}{\checkedsquare}\item\leavevmode}}

\title{Source Carriage Assembly Instructions}
\author{Ryan Bayes}
\date{\today}

\begin{document}
\maketitle
\section{Introduction}

This document describes the cleaning, handling, and assembly of the
elements of the source carriage. This includes the source pivot, the
UFO housing, and the source connector (top screw and nut). These parts
are not very well documented elsewhere, but they are key to the
assembly of the calibration hardware system. These pieces are permanently
fixed to the umbilical

\section{Part Descriptions}

\subsection{Source Pivot}
The source pivot is the upper most element of the source
assembly. This consists of a nut that fits snugly to the umbilical
with a rotating collar (the pivot) intended to provide a tie-off point
for the central rope. The pivot attaches to a pully flange, which
supports the fixed side rope pulleys, via a pin joint. The assembly
supports lower elements of the source via a pair of brackets. Design
drawings of the completed assembly are shown in Fig.\ref{fig:pivot}.

\begin{figure}
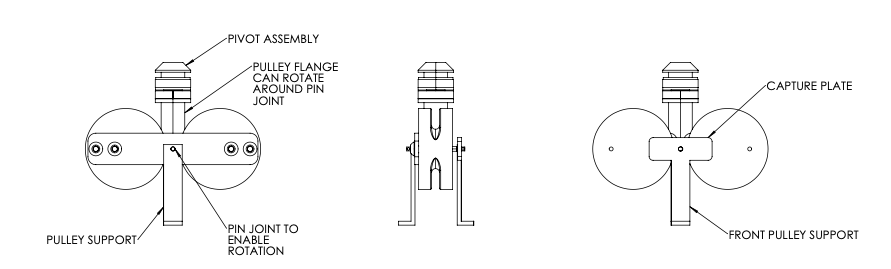
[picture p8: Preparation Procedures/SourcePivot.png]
  
  \caption{Source pivot and side rope pulleys}
  \label{fig:pivot}
\end{figure}

\subsection{UFO housing}
The umbilical flasher object (UFO) was intended to provide information
of the source location to the detector independent of the manipulator
system. As the central boards are not ready at this, this
functionality will not be available. However the housing for the UFO
will be used for the source assembly. The housing consists of a top
plate, an acrylic cylinder and a steel cylinder. The three pieces are
held together using long screws that connect the top plate to the
steel cylinder through conduits in the acrylic housing. The umbilical
is clamped into the UFO housing using a series of pressure plates that
are secured to the top plate. The source pivot also attaches to the
top plate of the UFO. Design drawings for the UFO cylinder and plate are
shown in Fig.\ref{fig:UFO}.

\begin{figure}
  \begin{center}
  \begin{subfigure}{0.4\textwidth}
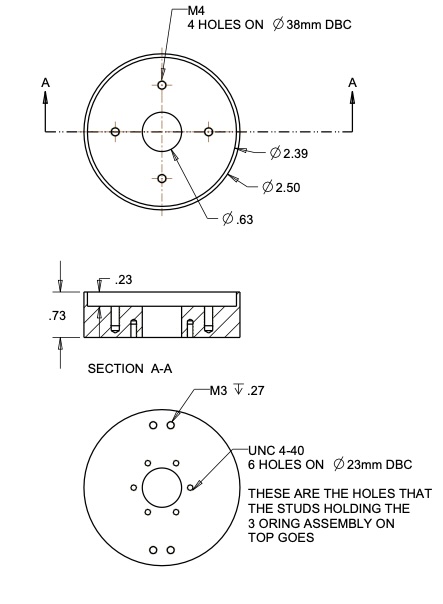
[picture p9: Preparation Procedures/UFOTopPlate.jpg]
    
    \caption{Top plate}
  \end{subfigure}
  \begin{subfigure}{0.4\textwidth}
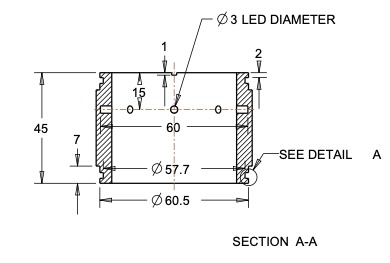
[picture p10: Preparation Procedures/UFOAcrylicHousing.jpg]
    
    \caption{Acrylic cylinder}
   \end{subfigure}
  \begin{subfigure}{0.4\textwidth}
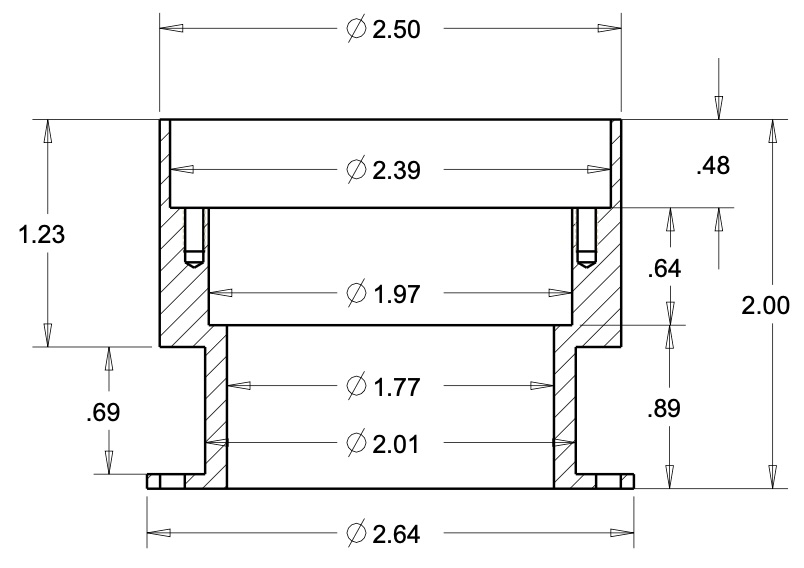
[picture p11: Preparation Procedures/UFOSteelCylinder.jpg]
    
    \caption{Steel Cylinder}
  \end{subfigure}
  \begin{subfigure}{0.4\textwidth}
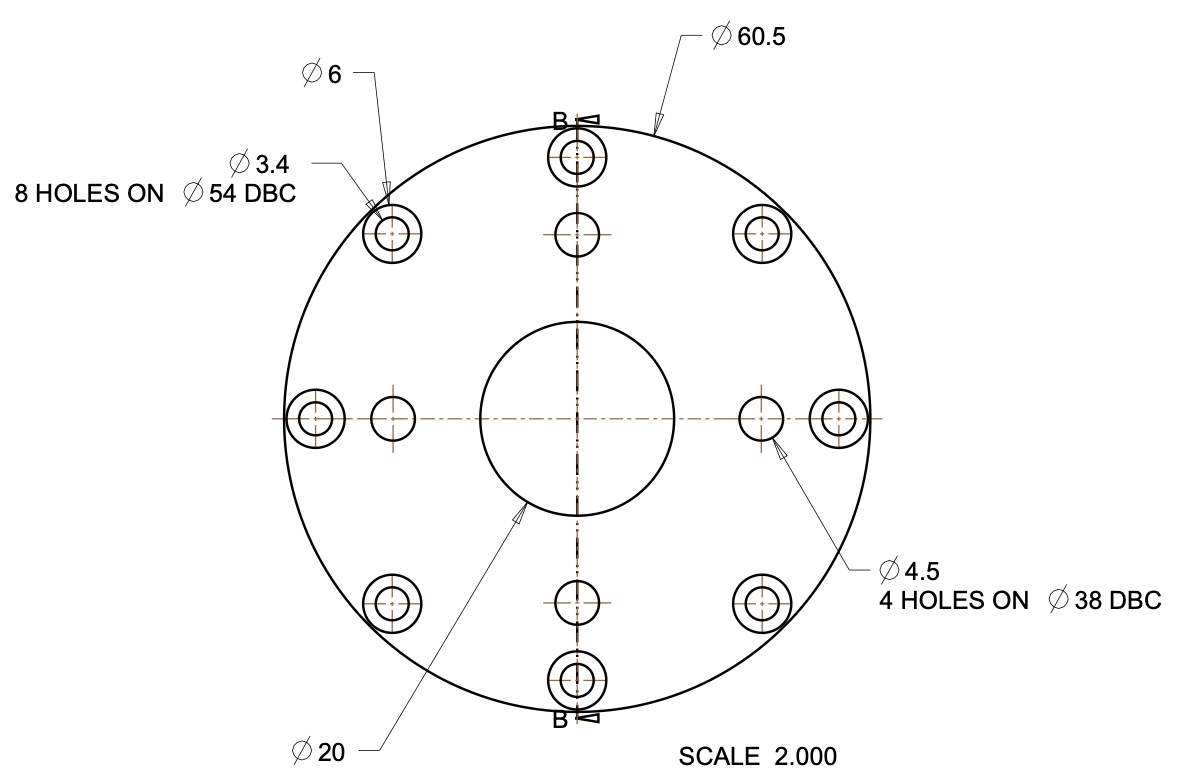
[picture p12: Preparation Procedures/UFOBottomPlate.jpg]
    
    \caption{Acrylic Bottom Plate}
  \end{subfigure}
  \caption{Umbilical flasher object housing}
  \label{fig:UFO}
  \end{center}
\end{figure}

\subsection{Source Connector}
The last permainent installation on the umbilical is the source
connector. This consists of a barrel with a left handed screw thread
on one end which is capped by a feed through which couples the optical
fibre in the umbilical to the quartz rod in the Laserball (which
terminates in a right hand thread source connector). The source
connector and a source (either the Laserball or the AmBe source) are
held together with a nut that contains corresponding threads (left
handed on the top half, right handed on the bottom half) such that the
umbilical side and the source side can be drawn together simply by
turning the nut in a clockwise direction while the umbilical and
source remain stationary. Alignment rods installed on the source
connector plates ensure the source and umbilical alignment through
source installation. A detail of the source connector is shown in
Fig.\ref{fig:SC} with a picture of the assembled source connector in
Fig.\ref{fig:SCP}.

\begin{figure}
  \begin{center}
\begin{subfigure}{0.4\textwidth}
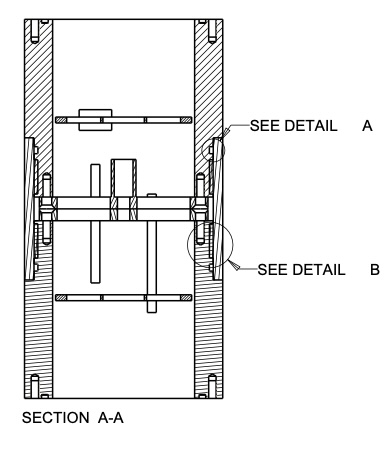
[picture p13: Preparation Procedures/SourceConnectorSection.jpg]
  
  \caption{Source connector detailed drawing}
  \label{fig:SC}
\end{subfigure}
\begin{subfigure}{0.4\textwidth}
  
  \caption{Source connector in hand}
  \label{fig:SCP}
\end{subfigure}
\end{center}
\caption{Source connector.}
\end{figure}

\section{Cleaning, Handling and Assembly}

All of the components of this assembly are stainless steel an
acrylic. It is assumed that the majority of cleaning for the various
components will be completed using ultra-sonic cleaning. The steps for
ultra-sonic cleaning involves
\begin{itemize}
\item Placing all of the items in the cleaner basket.
\item Fill the US cleaner volume with UPW
\item Add NuClean to the volume with a 1:50 concentration (NuClean to UPW)
\item Run the cleaner through a 60 minute cycle. This involves heating
  the volume to 60 degrees celcius, while applying ultra sonic
  frequencies.
\item Drain the cleaner with the components in place. Refill the
  cleaner volume with UPW. Run the cleaner for 30 minutes for a first
  rinse.
\item Drain the cleaner with the components in place. Refill the
  cleaner volume with UPW and run the cleaner for 60 minutes for a
  second rinse.
\item Drain the cleaner and remove the components from the ultra sonic cleaner
\item Dry all of the components with lint free cloths.
\item Place the components in plastic bags as appropriate.
\end{itemize}
Nitrile gloves must be worn at all times when handling the components
before, during and after the cleaning procedure.

At the present time, all of the parts for the source pivot assembly
are underground, the parts of the source connector and UFO housing are
on surface and were cleaned as part of the Laserball preparation, and
a second source connector assembly (for the AmBe source) is also on
surface and still to be cleaned. The parts that remain on surface are
intended to be taken underground by hand after triple bagging all of
the components. An additional plastic bag should be added for drift
travel, to be removed immediately upon entering the lab. The next most
outer bag should be removed before the assembly is moved to the
control room. The second to last layer should be wiped down with a
lint free cloth and UPW before the assemblage is moved to the DCR.

Assembly of the source carriage requires the cleaned and
installed umbilical and central rope. It may be reasonable to conduct a
limited pre-assembly of the source pivot well before the final
installation. Assembly consists of
\begin{answerlist}
\item Wet the bottom metre of umbilical with LAB
\item Pre-wet all of the screws with LAB
\item Install o-rings on the UFO acrylic cylinder, the source
  connector top and bottom surfaces.
\item Threading the umbilical through the pivot
\item Thread the umbilical through the pressure plates with appropriate o-rings.
\item Thread the umbilical through the top plate of the UFO.
\item Ensuring that there is a surplus of umbilical below the top
  plate of the UFO run the umbilical through the UFO acrylic, steel plate and
  stainless steel cylinder, and the upper source connector body.
\item Couple the end of the fibre bundle to the source connector plate.
\item Secure the source connector plate to the source upper source
  connector body with 8 m2 screws.
\item Fasten the UFO bottom plate to the top of the UFO steel cylinder.
\item Align the acrylic cylinder between the top section and the UFO
  plate and thread the support rods into the top plate. Once the
  threaded rod is secured, tighten the UFO assembly together using the
  appropriate nuts.
\item Fasten the UFO steel cylinder to the top of the upper source
  connector with 8 m3 cap screws.
\item Tighten the presure plates against the top of the UFO assembly
  using four M3 screws.
\item Secure the source pivot pully support plates to the UFO assembly.
\item Tie the central rope to the rotating collar on the pivot assembly.
\end{answerlist}

Questions:
\begin{itemize}
\item Do we have the pressure plates with the Laserball? Are these plates elsewhere?
\item Does the source pivot clamp down on the umbilical?
\item Is there enough room to turn a wrench to secure the threaded rod?
\item Is the fibre bundle assembly procedure written elsewhere?
\end{itemize}

\section{Usage}
Once the source connector has been assembled with the umbilical,
sources can be exchanged with little difficult. At this time only two
sources are planned; the Laserball and the AmBe source. Installation
of the laserball is the more sensitive of the two. The steps for this
involve two people equipped with standard PPE and nitrile
gloves. Assuming the source connector is exposed below the bellows
gate valve;
\begin{answerlist}
\item Remove the source connector end of the source from it's storage bag (leave the diffuser inside the bag).
\item Match the source connector to the umbilical source connector with the nut between them using the guide studs to locate the relative location of the two plates.
\item With the help of a collegue push the two source connector ends together until they meet the threads of the nut, then hold the source connector ends in place while turning the nut clockwise.
  \begin{itemize}
  \item If the nut does not thread easily, the nut will have to be flipped.
  \item If there is any resistance before the nut is completely threaded stop, check the orientation of guide studs and the alignment of the quartz rod before starting over.
  \end{itemize}
\item With the nut completely threaded, the complete source assembly should be snugly in place. Test by applying a little more force in the clockwise direction.
\item Remove the bag from the diffuser flask. Raise the source into the URM.
\end{answerlist}
These steps will be identical for the AmBe source except there will be be no guid rods to align as there is no optical rod to match.

\begin{thebibliography}{99}
\item[PulleyDesign] Mitchel Baker, ``Pulley Assembly July 9, 2021'', private communication
\item[SammyLB] Sammy Valder, ``The SNO+ Laserball Source for Scintillator Phase'', DocDB 7202
\item[KrausSC] Carsten Kraus, ``The Source Connector'', DocDB 
  
\end{thebibliography}

\end{document}

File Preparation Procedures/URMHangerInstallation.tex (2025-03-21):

\documentclass[11pt]{article}

\usepackage{geometry}                % See geometry.pdf to learn the layout options. There are lots.
\geometry{letterpaper}                   % ... or a4paper or a5paper or ... 
%\geometry{landscape}                % Activate for for rotated page geometry
%\usepackage[parfill]{parskip}    % Activate to begin paragraphs with an empty line rather than an indent
\usepackage{graphicx}
\usepackage{xcolor}
\usepackage{amssymb}
\usepackage{epstopdf}
%\usepackage{enumitem}
\usepackage{ulem}
\DeclareGraphicsRule{.tif}{png}{.png}{`convert #1 `dirname #1`/`basename #1 .tif`.png}
\usepackage{caption}
\usepackage{subcaption}
\title{URM Hanger Installation}
\author{Ryan Bayes}
\date{\today; V2}

\begin{document}
\maketitle

\section{Introduction}
The calibration deployment system needed to be updated in a number of ways to deploy sources in the scintillator filled UI. The URMs were redesigned to be leak tight and made out of scintillator compatible materials. Consequently, the URMs heavier than in water phase. Furthermore, it is assumed that the UI can move by as much as 8 inches vertically and 2 inches laterally. Finally, the gate valves selected for scintillator phase cannot take the torsional  stress of cantilevering a URM from it. For these reasons a new URM lifting system was designed. This new lifting and support system holds all of the weight of the URM independent of the UI assuming that the source tube is a flexible bellows.

The initial structural engineer design report indicated that the DCR Ibeam webbing cannot take the torsional stress of supporting the entire URM from the bottom flange alone, motivating a solution which supported the rear of the URM from below using a scissor lift cart and reinforced the front hanger to support the rails over the UI. The reinforced hanger is designed to wrap around the I-beam to reduce the stress on the interior webbing. The new design forces the installation team to work above the UI inside the DCR while breaking the DCR seal. As such, special precautions must be taken to keep the area outside of the working space clean.

\section{Definitions and Terms}
\begin{itemize}
\item {\bf URM}; Umbilical Retrieval Mechanism - System equipped to raise and lower sources by simultaneously manipulating the available length of a rope and umbilical attached to a source. 
\item {\bf URM Front Hanger} - A device clamped to the DCR I-beam which supports the URM over the UI by way of turnbuckles at the front of the UI. Also has rollers mounted for the lifting straps that support the rails when they are not supported by the turnbuckles. See Fig.\ref{fig:FHAClamp}.
\item {\bf URM Rear Hanger} - A device clamped to the DCR I-beam that supports the rollers for the rear lifting straps. It is not intended to lift the URM but it does provide some lateral safety during the lifting procedure. 
\item {\bf Scissor Cart} - A cart designed to support the URM and lift it to operating height prior to use. 
\item {\bf Lifting winch} - A device meant to wind straps that support the rails when not supported by the turnbuckles
\item {\bf Scaffold} - A temporary structure over the UI to be constructed specifically for this job, providing a foot path at least 152 cm (60 inches) above the Deck. The scaffold will have guard rails to prevent falls from the structure allowing workers to operate without harnesses and lanyards.
\item {\bf AV}; Acrylic Vessel - The centre of the SNO+ detector containing the active scintillator volume
\item {\bf AV neck} - A 7 metre long cylinder that connects to the spheroidal main body of the AV. 
\item {\bf UI}; Universal interface - The cap on the top of the AV neck consisting of the lower UI through which tubes for recirculation and extracting samples from the AV are connected, and the upper UI through which ports for gas lines, level sensors and calibration equipment exist. 
\item {\bf DCR}; Deck clean room - a tent in the centre of the SNO+ deck to isolate activities about the UI that may introduce contamination into the experiment from the rest of the lab. Is equipped with multiple hepa filters to circulate and clean the air that passes into the facility. 
%\item {\bf Radon monitor} - A 3 m$^{3}$ vacuum vessel used to measure levels of radon daughters in the cover gas volume. It is connected to the UI cover gas through a 1" diameter bellows hose. 
%\item {\bf Side rope motor box} - One of four boxes cantilevered off of the UI. Used to adjust the tension on the ropes used to guide sources in a 2-dimensional plane in the UI (either XZ or YZ). Necessarily connected to the UI cover gas through a 1/2" tube containing the side rope. All four motor boxes are equipped with quick connects to facilitate a clean connection to the UI cover gas space.
%\item {\bf Side rope extension box} - One of four boxes used to align the side rope with a feed through to enter the UI. Connected to the siderope motor box via a 1/2" inch tube with VCR connections on both ends. Connected to the UI cover gas through the rope feedthrough. Two extension boxes are equipped with valves to allow for clean connections to the UI cover gas.  
\end{itemize}

\section{Pre-Requisites}
Installing the URM front hanger will physically alter the DCR envelope with the potential for affecting the cleanliness of the environment. Precautions will be taken to make this as simple and efficient as possible. All of the parts must be identified and close at hand prior to starting work. Knowing the working environment well prior to the installation is essential for all workers. Safety is a number one priority and precautions must be taken to ensure that the installation goes ahead with a minimum of risk to the workers involved. The environmental considerations and risk mitigations are described below.

\subsection{Personnel}
\begin{itemize}
\item Task Lead: Ryan Bayes
\item Second: Matt Depatie
\item Further assistance: Parmesh Ravi, Stefan Kaluzienski
\item Scaffolding Assembly: Ben Zalan
\end{itemize}

\subsection{Parts and Equipment List}
\begin{itemize}
\item UI drop sheet
\item Temporary dust tent
\item Assembled scaffold over UI (Suggested height; 60 inches above DCR deck)
\item Knee pads for each of the workers involved (at least 2 pairs)
\item Heat resistant gloves for the workers (at least 2 pairs)
\item URM Front hanger consisting of
	\begin{itemize}
	\item Top plate (C-channel with 8 bolt holes for beam clamps on the wide surface and 3 bolt holes on the narrow surfaces)
	\item 2 side plates (L-bracket with 3 bolt holes near the end of the wide surface and 4 bolt holes on the narrow surface)
	\item Horizontal struts with bar installed using supports
	\item 16 beam clamp washers
	\item 16 stainless steel 5/8"-11 thread bolts, nuts and washers (8 partial washers to account for welds inside horizontal C-beam.
	\item 6 stainless steel 1/2" - 13 thread bolts  with 6 nuts and 12 washers
	\item 8 stainless steel 1/2" - 13 thread bolts  with 8 nuts and 16 washers
	\item 4 turnbuckles (install south pair only)
	\end{itemize}
\item URM Rear Hanger
	\begin{itemize}
	\item Horizontal struts with roller bar
	\item 8 beam clamp washers
	\item 8 zinc plated 5/8"-11 thread bolts, 
	\item 8 nuts and washers
	\end{itemize} 
\item new URM Winch 
	\begin{itemize}
	\item Winch assembly
	\item Old bolts to secure the winch to structural steel
	\end{itemize}
\item Wrenches
	\begin{itemize}
	\item 15/16" to secure the beam clamps
	\item 3/4" to secure the side plates
	\end{itemize}
\item Hex Socket wrenches
	\begin{itemize}
	\item 15/16" to secure the beam clamps
	\item 3/4" to secure the side plates
	\end{itemize}
\item Metal shears (sufficient to cut 1/8" aluminum)
\item 40"$\times$11" piece of tarp
\item Hot glue
\item Hot glue gun
\item cordless drill (with charged battery pack)
\item 3/8" hex drill socket
\end{itemize}

\begin{figure}[htbp]
\begin{center}
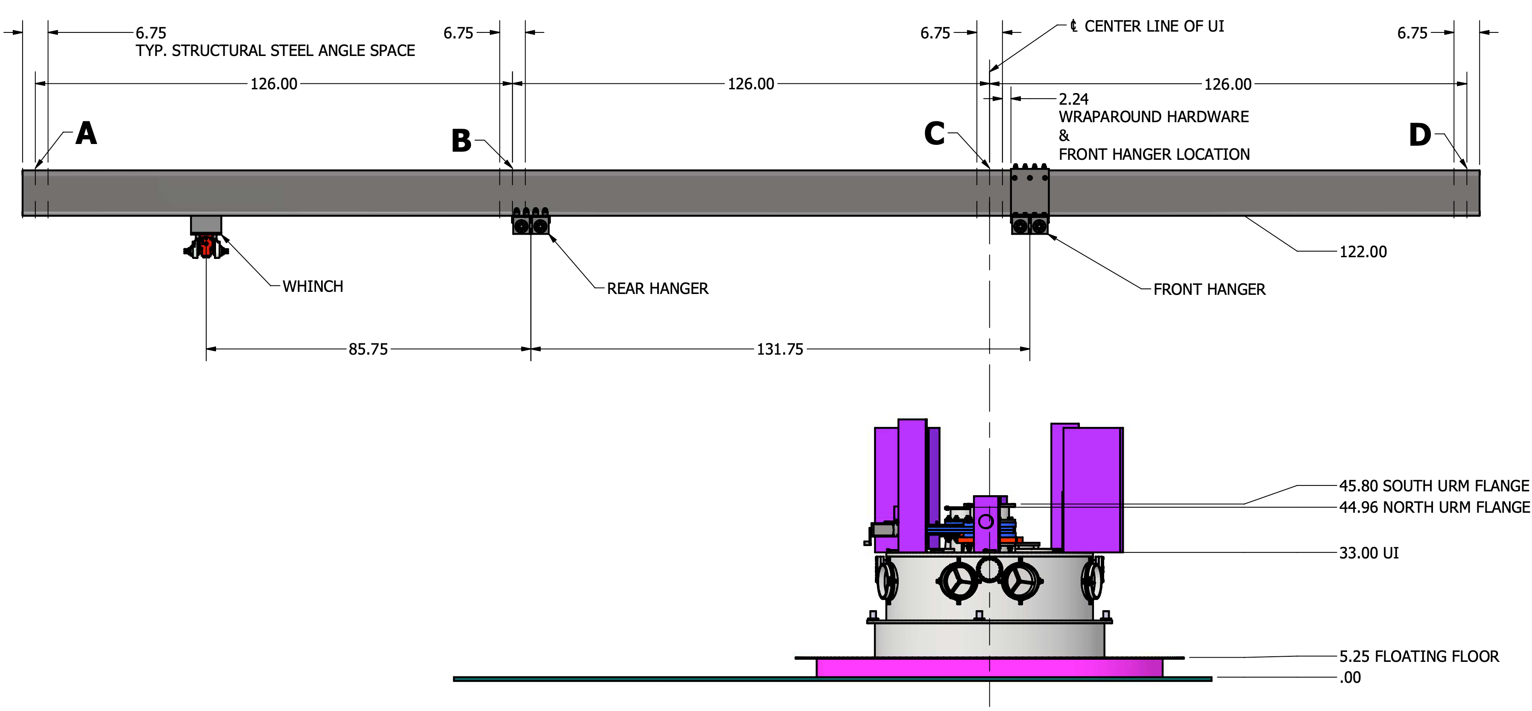
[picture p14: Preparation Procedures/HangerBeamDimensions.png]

\caption{Location of the hangers and winch on the beam relative structural steel indicated (UI viewed from the South).}
\label{fig:hangerloc}
\end{center}
\end{figure}

\begin{figure}[htbp]
\begin{center}
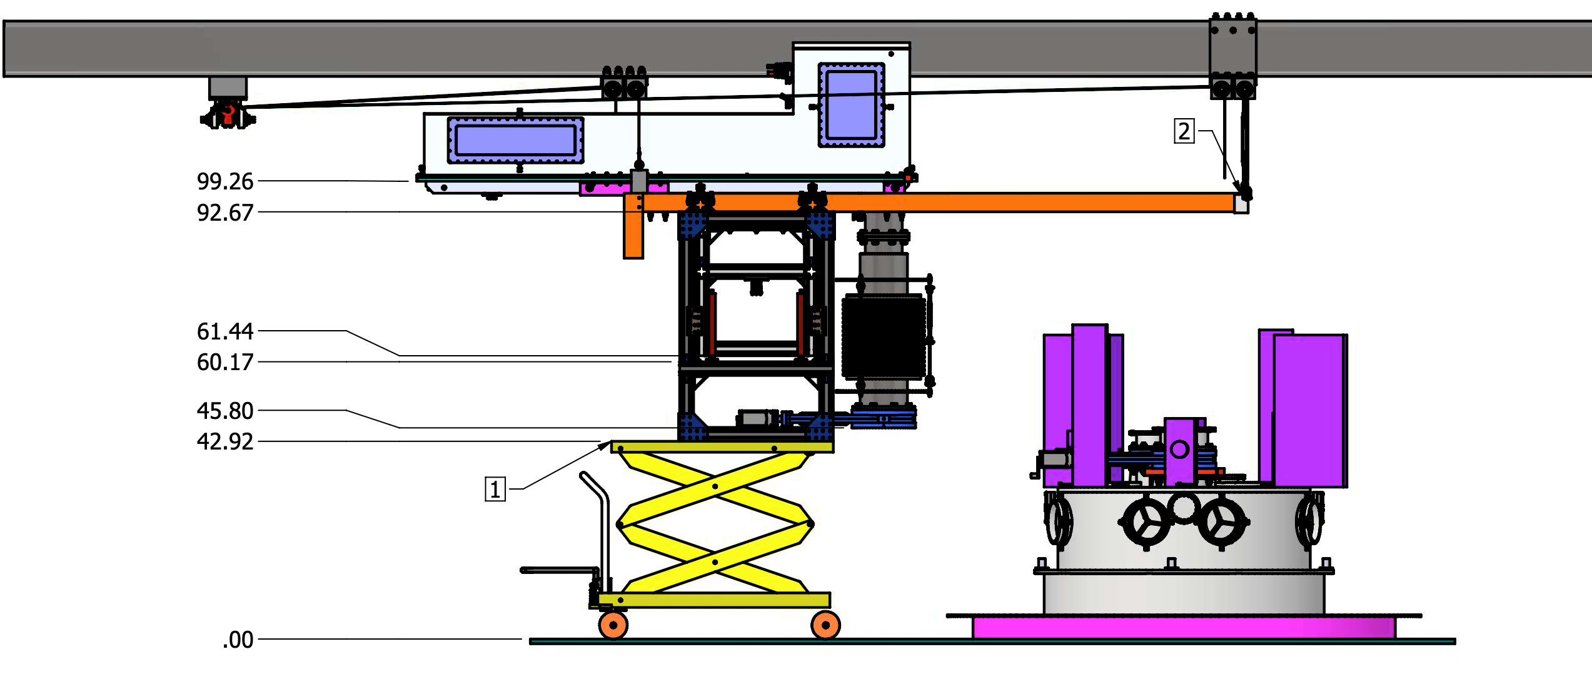
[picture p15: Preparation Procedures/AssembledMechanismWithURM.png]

\caption{Assembled URM support system with the vertical dimensions of the various components.}
\label{default}
\end{center}
\end{figure}

\subsection{Environmental considerations}
When designing the new URM front hanger, the primary consideration was structural strength given the load at the required toque. No consideration was made to the integrity of the clean tent. The tent will need to be altered to renew the seal on the tent after the hanger installation. As a piece of c-channel is to be used to enclose the I-beam from the top, a breach must be made in the DCR tent. The tent will have to be resealed against the I-beam. At present the a tarp bag is suspended about the I-beam using a pair of 1"$\times$1" L-brackets clamped to the edge of the top face of the beam. These angle brackets will need to be removed and replaced with a series of shorter L brackets. The suggested approach is to replace the Then the bag can be rehung and closed. 

The DCR tent itself is sealed against the I-beam using double sided tape. Gaining access to the beam is as simple as pealing the tarp from the tape in a long enough section to complete the installation with a few small cuts to allow the remaining sections to be left in tact. A method to reseal the tarp after installation of the clamp would be to thread a piece of tarp underneath the vertical plates of the hanger so that the lower strut clamp grabs on to the new tarp and the bag. The new piece of tarp could be resealed against the I-beam and then threaded around the top bracket of the hanger so that sealing the tarp against itself forms a pocket for the top flange. If the piece of tarp cut from the DCR roof is threaded between the two vertical plates prior to bolting them together, the new seal can be produced while providing tension to the DCR roof.

The location of the hanger to be installed is offset 10cm from the centre-line of the acrylic vessel. This location is covered on the outside of the DCR tent with a plate that supported the feedthroughs for the SNO side rope motor boxes. This plate will need to be navigated during the installation of the plate to go over the I-beam which is considered feasible as the planned c-channel to be used for the upper part of the hanger clamp will be 3.45" high and the plate is supported 4" from the I-beam. However, the plate may help while the tent is breached as it will also serve as a partial dust shield from the deck environment.

The hanger installation will involve exposing the I-beam so a drop cloth must be placed over the UI to keep potential flakes from the I-beam or material from the scaffolding assembly from falling on the UI. The proposed drop cloth will be composed of polysheet plastic and should cover the UI out to the edge of the sliding floor. A partial dust tent should be maintained around the scaffolding during the installation itself to control the spread of dust to the immediate vicinity. 

\begin{figure}[htbp]
\begin{center}
	\begin{subfigure}{0.45\textwidth}
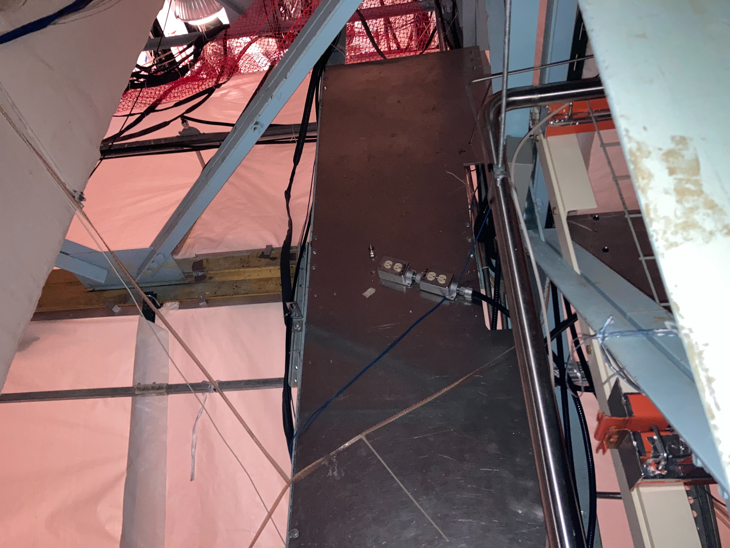
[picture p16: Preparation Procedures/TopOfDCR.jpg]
	
	\caption{View of the top of the DCR from the existing covergas scaffolding.}
	\label{fig:topofDCR}
	\end{subfigure}
	\begin{subfigure}{0.45\textwidth}
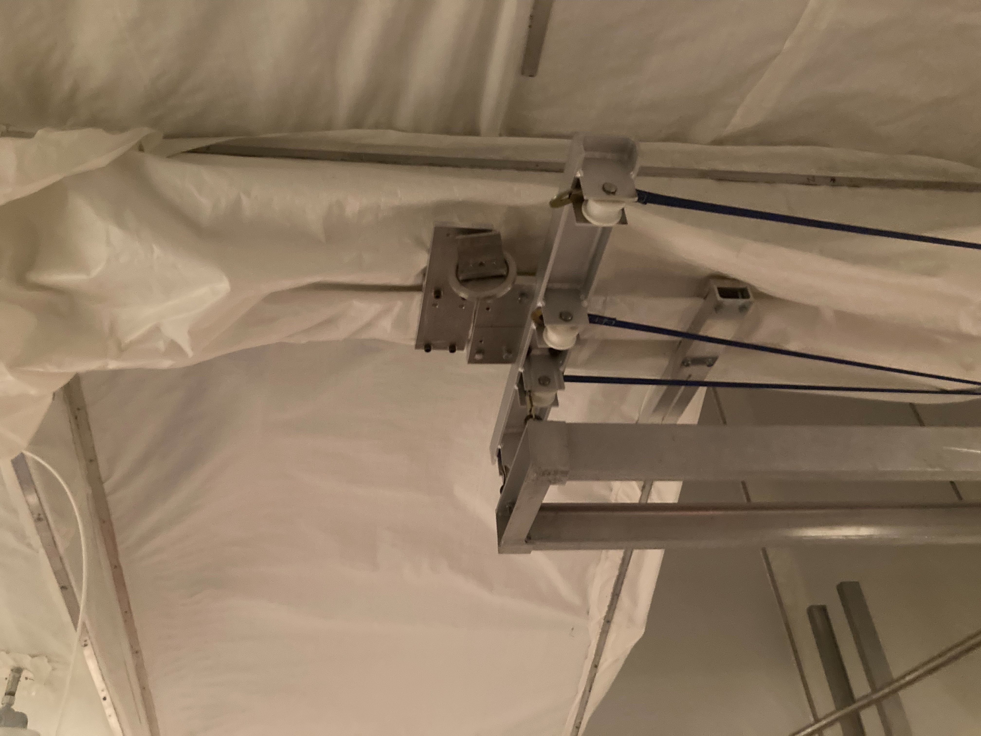
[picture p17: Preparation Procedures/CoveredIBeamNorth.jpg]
	
	\caption{View of the North face of the covered I-beam}
	\label{fig:cvIbeamN}
	\end{subfigure}
	\begin{subfigure}{0.45\textwidth}
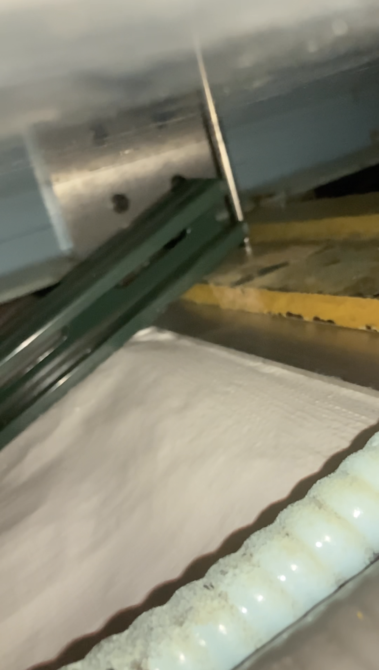
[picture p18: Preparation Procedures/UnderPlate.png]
	
	\caption{View of the underside of the SNO siderope plate.}
	\label{fig:belowplate}
	\end{subfigure}
	\begin{subfigure}{0.45\textwidth}
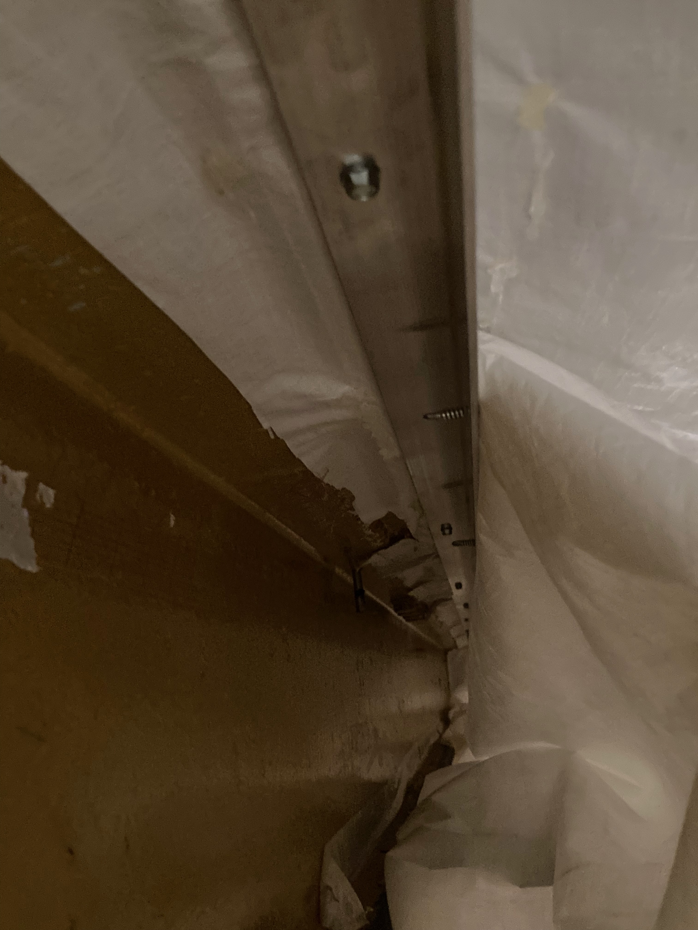
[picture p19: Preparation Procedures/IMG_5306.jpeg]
	
	\caption{The DCR I-beam inside the bag}
	\label{fig:inbag}
	\end{subfigure}
	
%	\begin{subfigure}{0.45\textwidth}
%	\includegraphics[width=\textwidth]{CoveredIbeamSouth}
%	\caption{View of the South face of the covered I-beam}
%	\label{fig:cvIbeamS}
%	\end{subfigure}
\end{center}
\end{figure}

\begin{figure}[htbp]
\begin{center}
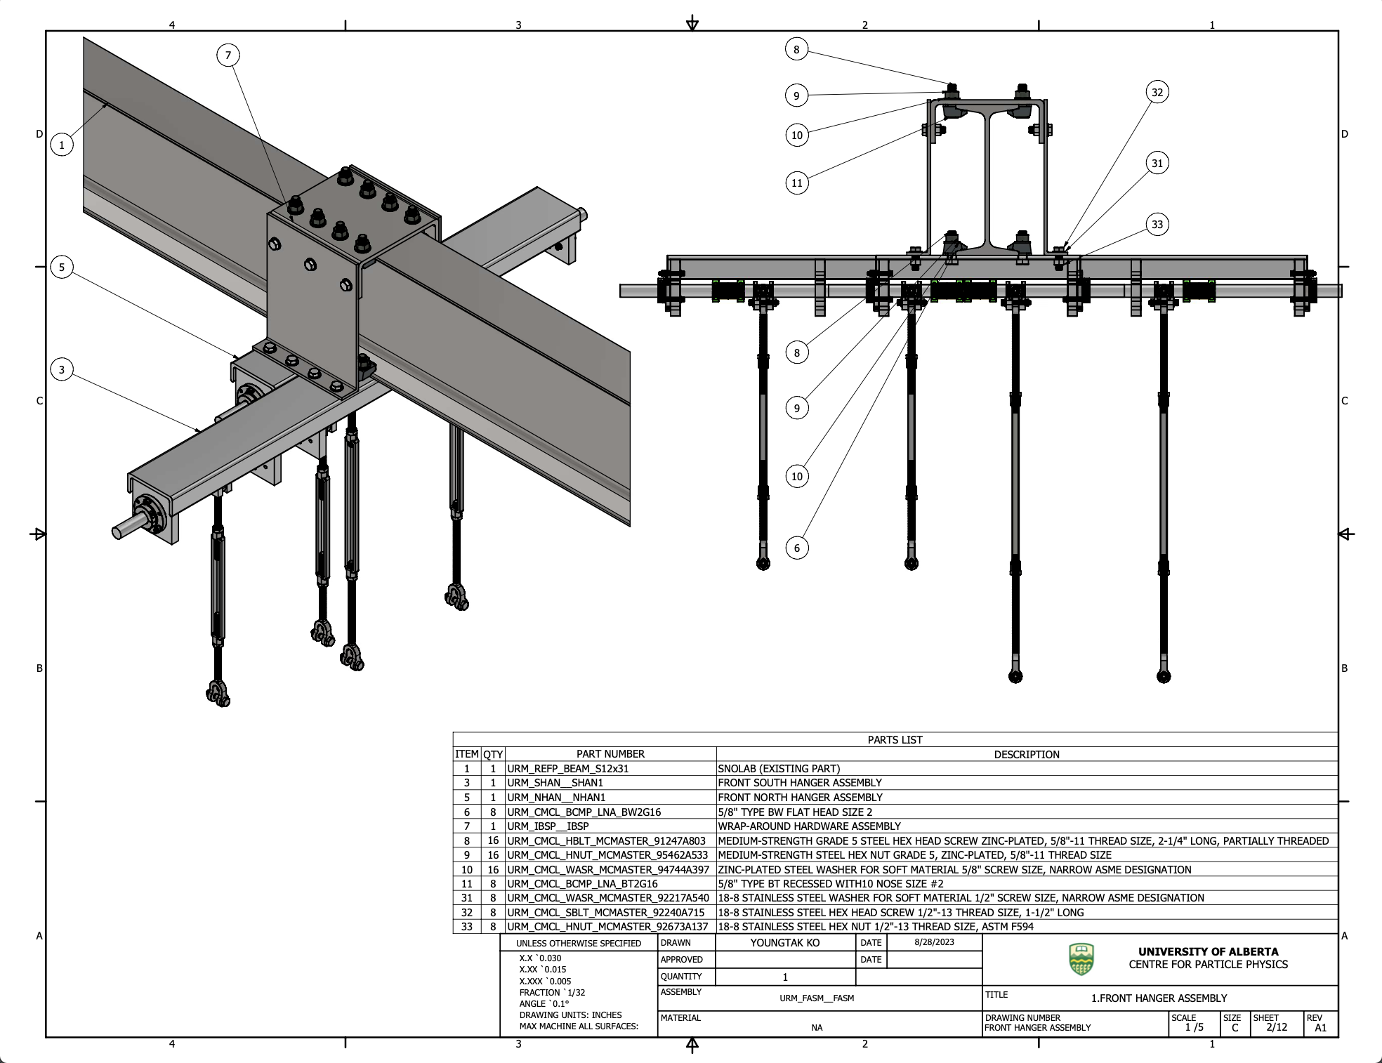
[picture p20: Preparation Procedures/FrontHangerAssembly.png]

\caption{Front hanger assembly showing the wrap around I-beam clamp}
\label{fig:FHAClamp}
\end{center}
\end{figure}

\subsection{Risks and Mitigation}
To install the wrap around hanger, the workers will be operating at a height at least 60 inches or 170 cm above the deck over the UI. Given that the UI has sensitive equipment on it, using the UI as a platform is not ideal, and ignoring that, the UI is an unstable surface without a rail. Therefore it is assumed that all of the following work will be done using a scaffolding over the UI with a rail in place that can prevent harm to workers or equipment due to potential falls. The scaffold should straddle the UI along the East-West axis to provide access to the length of the I-beam over the UI.  To make the work more ergonomic the scaffolding should be placed so that workers can reach over the DCR ceiling comfortably. This forces a condition where the workers will be working from their knees most of the time; kneepads will be required for the workers. 

\section{Procedure}

\subsection{Pre-Installation Procedures}
\begin{enumerate}
\item Pre-assemble the front hanger off of the I-beam (in the DCR or clean lab) to familiarize all workers with the assembly of the device prior to assembly on the I-beam. Check that all parts will work as intended. 
\item Position drop cloth over UI.
\item Install scaffolding over UI. Vacuum the area around the scaffolding after installation
\item Remove hardware from old lifting mechanism (exception: it may be of value to leave the old front cross-brace to support the side plates during installation instead of installing the new horizontal strut temporarily before moving it to install the bag.)
\item Install dust tent around the scaffolding and secure it to the edge of the UI drop cloth (with clothes pins).
\end{enumerate}

\subsection{Front Hanger Installation Procedure}
\begin{enumerate}
\item Remove strapping securing the I-beam bag from the L brackets on either side of the I-beam. The beam must be exposed to the planned installation position.
\item Peal the DCR tent tarp off both sides of the I-beam in the hanger location. 
\item Cut away a 9" section of the L-bracket from the proposed location of the hanger on both sides of the I-beam. Loosen the screws between the L-bracket and the strapping on the outside of the tent on either side of the work area without completely removing the screws. If adequate shears to cut into the 1/8" aluminum can be identified this can be done in situ; otherwise the whole L-bracket will need to be removed from the DCR and the L-bracket will be cut into the appropriate lengths in the utility drift using a hacksaw with appropriate clean room precautions.
\item Cut  9" wide panels into the tarp to gain access to the top of the I-beam from the tent on both sides of the I-beam. Do not remove the panels from the rest of the tent material. 
\item Cut a matching section from the strapping over the top of the I-beam. If the screws between the angle bracket and the upper strapping has been loosened tighten it again. 
\item Place the upper plate of the hanger over the I-beam. Ideally this should be done from below by sliding the c-section over the I-beam. Clamp the plate to the top flange of the I-beam using the six beam clamps. Allow the free panel of tarp to hang outside of the plate.
\item Secure a piece of tarp 40" in length and 11" in width to the I-beam with double sided tape with enough slack on either side to fold around the downward flange of the top plate of the hanger. Temporarily secure the ends of the tarp with clothes pins. The edges of the tarp should be glued together to make a pocket around the plate. 
\item Lift one of the side plates and align the bolt holes between the top plate and the side plate with the loose end remaining from the ceiling tarp between plates with the free tarp. Puncture all three layers of tarp at each of the three bolt points with an awl or similar tool to ensure alignment. Repeat with the second side plate.
\item Patch the remaining gaps in the tarp with what slack remains from the patch tarp using hot glue. 
\item Disconnect the horizontal arms of the hangers from the vertical plates and I-beam.  
\item Replace the bag along the I-beam by replacing the strapping along the L-bracket. At the front hanger, simply bend the strapping around the plate as necessary.
\item Reconnect the horizontal arms of the hanger with the vertical hanger plates below the bag. Holes will have to be pushed through the bag to accommodate the bolts. Clamp the horizontal arm to the bottom flange of the I-beam using the beam clamps through the I-beam bag.
\item Install the rear hanger by clamping hanger to the lower flange of the I-beam through the bag. 
\item Install the winch using at the former lifting mechanism 
\end{enumerate}

\subsection{Post Installation Procedures}
\begin{enumerate}
\item Clean the interior of the dust tent. Vacuum the surfaces of the scaffolding, and wipe the walls of the dust tent. 
\item Remove the dust tent from the work area.
\item Install hardware on the hanger including straps and turnbuckle.
\item Disassemble the scaffold
\item Remove the UI drop cloth
\item Clean the DCR, starting with the walls and working toward the UI; outer surfaces, vacuum floors, and UI.
\item Repeat cleaning the DCR.
\end{enumerate}

\section{Afterward}

Once this procedure is completed, in situ testing must be completed. The operation of the winches should be tested with the rails alone before any further tests. Alterations must be made to the rails including the front plate and the mounting points at the rear of the rails prior to use with lifting mechanism.  Further testing with the URM will require the parallel completion of the URM scissor table as well as the installation of the URM wheel mounts. Any URM commissioning activities should be completed either before this procedure is complete, or sufficiently isolated in time that the DCR is returned to a clean room status with fewer than 200 counts of 0.5 $\mu$m particulates per $m^{3}$. Presumably this includes multiple complete cleanings of the DCR.

\end{document}

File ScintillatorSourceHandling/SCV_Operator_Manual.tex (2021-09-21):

\chapter{Source Cleaning Apparatus Manual}
\section{Purpose}
This document describes the necessary information and standard procedures that \textbf{must} be followed for the operation and handling of  the source cleaning vessel. In case a part or step of this procedure is not clear or a statement in the procedure contradicts the state of experiment, do not continue with the process. Contact the calibration coordinator and detector manager and get permission to proceed 
\section{Definitions}
\textbf{Cleaning Module}: An apparatus that can be attached directly to the source tube gate valve that sprays a flow of LAB directly onto a source to facilitate cleaning. The set up allows to draw LAB for testing .\\
\\
\textbf{Source Connector}:A device by which a source may be temporarily connected to an umbilical while also allowing bre optic or electrical connections.\\
\\
\textbf{Umbilical Retrieval Mechanism(URM)}:The device in which the umbilical is stored
in preparation for deployment that also includes drive mechanisms for the central rope and umbilical to facilitate vertical movement of sources.\\
\\
\textbf{Source Tube}: A tube connecting to the bottom of the URM with a bellows below that terminates on a gate valve that connects to a nipple assembly on the UI when the URM is in a position ready for deployment.\\
\\
\textbf{Umbilical}: A length of Tygothane tubing containing an optical fiber and five electrical wires to which calibration sources are attached for deployment in the AV.\\
\\
\textbf{Boil Off Nitrogen}: Nitrogen sourced from a cryogenic nitrogen dewar that is installed in the Utility drift and is transferred  to the DCR by way of copper conduit (high pressure) or from the international dewar (low pressure). The pressure of the high pressure nitrogen boil off  for purging purposes must be regulated using the gas board in the DCR to less than 20 psi. ( @ Ryan Reference to the relevant procedure required )\\
\\
\textbf{Linear Alkyl Benzene(LAB) cleaning set up}: This setup is designed to clean the LAB. The complete unit consists of different parts such as pump, filters, pulsation dampener, piping system, fitting and cart.\\
\section{Description of the Cleaning Module}
The cleaning module consists of a  31.78" long cylindrical tube with 9.50" interior diameter. Inlet and outlet gas connections are supplied to allow nitrogen flushing of the module independent of the URM system. Four LAB sprayers near the top of the cleaning module provide a stream of LAB to actively rinse the source. The flange at the top of the source allows  to connect the cleaning module to the gate valve at the bottom of the URM source bellows. A cart with a jack is provided to move and lift the cleaning module into position, and provide a clean working surface for source work.
\begin{figure}[!htpb]
  \centering
  
  \caption{Line Diagram of the LAB cleaning set up}
  \label{fig:SCV}
\end{figure}
\\
\section{Important points and prerequisite}
Before commencing any activities related to the source cleaning vessel and LAB set up, the designated people should follow these steps:
\begin{enumerate}
\item The Safety Data Sheet (SDS) must be thoroughly reviewed each time when handling LAB. Permission from the detector manager must be obtained in writing.
\item All person must be equipped with required PPE ( Nitrile gloves, masks, safety glasses, head cap) before the starting of any procedure and change them as required.
\item The vessels must be handled with fresh, clean gloves and face masks must be used by the individuals involved in the activity.
\item  When moving the vessels, there must be at least three people present: one will be the “dirty” person, the other two “clean”.
\item The “dirty” person must keep an eye on the clean persons at all time and ensure that the clean persons not get in contact with any unclean surface.  If in any case it happen then instruct them to change their PPE.
\item Every piece of equipment that will receive parts or need additional items like wrenches, screw drivers etc. need to be set up first (checked, cleaned and put in appropriate location etc) before the vessel is moved, or used.
\item The receiving parts must be thoroughly cleaned with Ultra Pure Water(LPW). 
\item No clean part should be touched without clean gloves and masks on.

\end{enumerate}

\section{Procedures}
The following procedures must be done within the deck clean room and all necessary protocols must be followed. It is assumed that the operator is to perform all operations using latex gloves in addition to standard Personal Protective Equipment (PPE). Dust counts should be monitored prior to operations involving opening the  URM source tube or exposing a source. If the dust count appears to be high, the DCR should be cleaned and the intended procedure should be suspended. All procedures listed here should be completed with the participation of a calibration expert.

\subsection{Connecting the URM to the UI}

\subsection{Disconnecting the URM from the UI}

\subsection{Using the Source Connector}

\subsection{Attaching a Source to the Umbilical}\label{ss:sourceattach}

 The instructions below presuppose that the source is not connected to the umbilical. Note that the following only applies to the North side URM as the South side URM will have the Cherenkov source permanently attached to its umbilical. Sources of LAB, and boil off nitrogen should be procured before attempting the following procedure.

\begin{enumerate}
\item Begin with the source in the cleaning module
\item Start the flushing the cleaning module with N$_{2}$ 
\item Move the URM back from the UI over the working area West of the UI
\item Position the cleaning module cart under the URM
\item Close the URM cover gas bag and start actively flushing the URM with N$_{2}$
\item Open the gate valve and lower the source connector until it can reach the source.
\item Connect the source to the umbilical via the source connector. 
\item Raise the source into the source tube
\item Connect the cleaning module to the source tube gate valve
\item Make connections (Can be done by any one of the two clean person) for the  airline fitting at the specified port on the  LAB cleaning set up for starting the pump.
\item Check the connection for the inlet of LAB cleaning set up with LAB supply vessel (Ensure that the vessel  is filled with the minimum level (approximately 10 litre) of LAB required for the cleaning procedure ).
\item Set the bottom MV1  toward the injection line and the MV3 toward  line to the vessel.
\item Start the pump by providing the pressure from the Air line ( Maximum upto 125 psi, Pressure can be controlled by the pressure control valve) and allow LAB to flow in the LAB cleaning set up.
\item Wait until an adequate amount (When a 2/3 volume of the bottom conical part in the source cleaning vessel is filled with the LAB) of LAB is pumped in the LAB cleaning set up.
\item Once the adequate amount of LAB is filled  in the LAB cleaning set up then stop the pump and set the MV1 toward the recirculation line.
\item Turn on the pump again and allow LAB to flow in the LAB cleaning set up.
\item While the LAB flowing  lower the source through the LAB stream. The source should be  raised and lowered through the spray to remove surface contamination. The initial rinse should continue until the source (and the source connector) are clean.
\item Monitor the O$_2$ levels in the URM to validate the cover gas viability. The URM radon levels should also be monitored directly using the RAD7. The cover gas should be considered viable after the measured radon levels are consistent with zero. Once the cover gas is deemed viable the N$_{2}$ flush can be terminated and the cover gas bags can be opened to the URM. 
\item Take a sample to be submitted for analysis. To collect samples, set the manual MV2 at the On position, after collecting samples set the valves again at the off position.
\item Repeat spraying the source with LAB as above until the source get sample analysing . Allow the source to sit in the LAB for some time (order of a week) periodically draining the LAB, submitting samples for analysis . Record the status of the LAB cleanliness for each sample preparation (need to define a quantifiable cleanliness criteria)
\item Once the LAB cleanliness criteria is reached (TBD) the source should be raised into the source tube, the gate valve closed and the cleaning module disconnected from the gate valve. 
\item Move the URM back to the UI and reconnect the gate valve to the nipple assembly on the UI
\item Once the cleaning operation is complete, then the remaining LAB from the processing lines can be flushed out from the LAB cleaning set up by using the “dump” line. 
\item To do this, again turn off the pump, set the MV3 to the “dump” line where it should be connected to a container to accumulate the fluid. 
\item Then turn the pump on and pump until there is no more fluid exiting the dump line. Note that this will remove the majority of the fluid, but there will always be some fluid left within the process lines. 
\item Turn off the pump by stopping the pressure from the Air line at the specified port. 
\end{enumerate}

\subsection{Cleaning a Source Prior to Use}
Here, the minimum guidelines for cleaning a source should be set out. Each group should have their own specific cleaning instructions which should be compiled with this document. However, prior to use each source should
\begin{enumerate}
\item be inspected by a designated person to look for signs of corrosion or damage to the source
\item be wiped down using ultra pure water to initially pick up surface contaminants
\item be wiped down with an alconox mixture to futher remove surface contaminants
\item be wiped down with ultra pure water again to remove the alconox
\end{enumerate}

\subsection{Detaching a Source from the Umbilical}
Required for this procedure is a storage module for the source. This module should be connected to a pump/purge system to keep the source in a nitrogen environment between uses.
\begin{enumerate}
\item Ensure that the source storage module is available for use on the source cart.
\item Disconnect the URM from the UI.
\item Move the URM back to the working area and place the source cart in the working area
\item Disconnect the URM cover gas bag and flush nitrogen through the URM.
\item Open the source tube gate valve over the working surface of the source cart.
\item Lower the source to the working surface of the source cart.
\item Disconnect the source from the umbilical at the source connector.
\item Place the source in the storage module. Close the storage module and pump nitrogen into the storage module.
\item If a new source is not to be immediately connected to the umbilical, retract the source connector back into the URM source tube and close the gate valve. Continue the URM purge until O$_{2}$ monitor and RAD7 values are below established thresholds before the cover gas bags are reconnected. 
\item If a new source is to be reconnected refer to Section \ref{ss:sourceattach}.
\end{enumerate}

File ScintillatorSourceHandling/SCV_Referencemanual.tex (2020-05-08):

\chapter{Source Cleaning Vessel Reference manual}
\section{Introduction and Purpose}
The Source Cleaning Vessel (SCV) is an apparatus for the cleaning of calibration sources and comprises a cylindrical tube, plugs, flanges, conical base and spray nozzles. The central part of the vessel is made up of a  cylindrical tube and connected with the top and bottom parts through flanges. The nozzles from top and bottom uniformly spray Linear Alkyl Benzene (LAB) on the source  and the drain port in the base allows to collect the liquid to return to the pump or for sampling and testing.The following document describes all information regarding the SCV and its related parts and it provides hyperlinks to references and suppliers. Figure~\ref{fig:SCV} depicts its dimension and associated parts.
\begin{figure}[!htpb]
  \centering
  
  \caption{Source Cleaning Vessel}
  \label{fig:SCV}
\end{figure}

\section{ Definitions and Parts of the SCV}

\textbf{Cylindrical tube}: \\
It embodies the central part of the vessel that accommodates the source.\\
\\
Purchased From: Johnston industrial plastics limited\\
\\
Link:  \url{https://www.johnstonplastics.com}\\
\\
Dimension for the vessel: 9.50$''$(ID) x 0.25$''$(Thickness) x 30.84$''$(Length).\\
\\
Material: Cast Acrylic.\\
\\
**I will add a final drawing.\\
\\
\textbf{Plug rings}:\\
These are small rings to hold the bulkhead fittings.\\
\\
\begin{figure}[!htpb]
  \centering
  
  \caption{Drawing of the plug ring}
  \label{fig:plug}
\end{figure}
\\
Dimension: 0.43$''$(ID) x 0.25$''$(Thickness) x 0.73$''$(Length).\\
\\
Material: Acrylic ( Rod from physics workshop)\\
\\
/%\begin{figure}[!htpb]
 % \centering
  %\includegraphics[width = 7cm, height=6cm ]{figures/plug1}
  %
  % \includegraphics[width = 7cm, height=6cm ]{figures/plug2}
  %\caption{Plugs for bulkhead fittings}
  %l\abel{fig:plug1}
%\end{figure}
%
\\
\textbf{Flanges}:\\
Dimension for one of the service flange that we have machined for our test design:\\
\\
9.75$''$(ID) x 0.50$''$ (Thickness) x 11.80$''$(Length) \\
(I will add drawings of other flanges according to our final design once I got from Mitchel) .\\
\\
Material: Acrylic ( Acrylic sheet from lab L2-92)\\
\begin{figure}[!htpb]
  \centering
  
  \caption{Drawing of the service flange}
  \label{fig:flange}
\end{figure}\\
\textbf{Conical Base}:
It is the bottom part of the vessel with a conical shape and provides a drainage port to collect LAB. The conical geometry allows the used fluid to drain from vessel.\\
\\
Material: Acrylic(Acrylic sheet from physics lab)\\
\begin{figure}[!htpb]
  \centering
  
  \caption{Drawing of the Conical base}
  \label{fig:base}
\end{figure}
\\
\textbf{Spray Nozzles}:
The Spray nozzles are simple devices used to break apart a fluid flow into a spray pattern. It is one of the crucial parts of any cleaning system and needs to be chosen appropriately for effective cleaning. There are many variables that should be explored and investigated before the selection of suitable nozzles for any cleaning system. The variables are as follow:\\

\textbf{Dust particle size} \\                                              

\textbf{Spray drop size}\\

\textbf{Spray pattern}\\

\textbf{Spray angle}\\

\textbf{Operating pressure}\\

\textbf{Nozzle placement}\\
\\
Keeping in mind these requirements and after exploring all the variables according to the need of our system, we have chosen Full cone wide-angle ( 112 and 120 deg) hydraulic nozzles(Figure~\ref{fig:nzl})
\begin{figure}[!htpb]
  \centering
  
  \caption{Full cone wide angle nozzle}
   \label{fig:nzl}
\end{figure}
\\
Purchased from: Spraying system Canada ltd.(\url{ https://www.spray.ca}\\
\\
Material: Stainless steel 316\\
\\
Part Number: 1/4G-316SS4.3W \\
\\
In our case, we have placed nozzles on the top and bottom to rinse the source from all sides.\\
\\
\textbf{Bulkhead Fitting and O rings}: \\
\\
\textbf{Bulkhead fitting}:
It is an item that is designed to allow a connection through the wall of a container or vessel. The details of the fittings that we are using are follow:\\
\\
\begin{figure}[!htpb]
  \centering
  
  \caption{Swagelog bulkhead fitting}
  \label{fig:ftng}
\end{figure}
\\
Purchased from: Swagelok Edmonton Valve and Fitting Inc.\\
\\
Material: Stainless steel 316.   \\                           
\\
Part Number: SS-400-11-4\\
\\
Connection type: Bulkhead Male Connector, 1/4$''$Tube OD x 1/4 $''$Male NPT\\
\\
\textbf{O rings}: 
\\
They are commonly used in sealing applications. In our operation we are using chemical resistant Viton Fluoroelastomer O-Ring with the bulkhead fitting for the airtight sealing.\\
\\
Purchased from: McMASTER-CARR.\\
\\
Material: Viton® Fluoroelastomer Rubber\\                                
\\
Part number: 9464K17\\
\\
\url{https://www.mcmaster.com}\\
\\
\begin{figure}[!htpb]
  \centering
  
  \caption{Viton Fluoroelastomer O-Ring}
  \label{fig:oring}
\end{figure}
\\
\section{ Linear Alkyl Benzene (LAB) cleaning set up}
This setup is designed to provide clean LAB for the cleaning of SNO+ sources . The complete unit consists of different parts such as pump, filters, pulsation dampener, piping system, fitting and cart.  LAB is noncorrosive (SDS) hence doesn’t demand any specific storage but from previous experience and observations, it is recommended to use stainless steel and PTFE wetted parts only, LAB is known to swell and degrade elastomers over time. \\
\\
\textbf{Parts of LAB set up}:\\
The details of all the parts associated with the unit are as following:\\
\\
\textbf{Piping system and fittings}:\\
\begin{itemize}
\item  1/2$''$ 316 stainless steel tubing with a wall thickness of 0.049$''$: \url{https://www.mcmaster.com/89785k845}.
\end{itemize}

The list of fittings includes:\\
\begin{itemize}
\item Four hose connections (1/2$''$ to 3/8$''$): SS-815-6: \url{ https://www.swagelok.com/en/catalog/Product/Detail?part=SS-815-6}
\end{itemize}

\begin{itemize}
\item Four 1/2$''$ unions: SS-810-6 
\end{itemize}

\begin{itemize}
\item Five 1/2$''$ MNPT to Female Swagelok Connect: SS-810-1-8 
\end{itemize}

\begin{itemize}
\item One 1/2$''$  MNPT to Male Swagelok connect: SS-8-TA-1-8 
\end{itemize}

\begin{itemize}
\item One 3/4$''$ MNPT to Male Swagelok connect: SS-8-TA-1-12
\end{itemize}

\begin{itemize}
\item Three   1/2$''$ tees, and one  1/2$''$ tee with a 1/4$''$ connection: SS-810-3: 
\end{itemize}

\begin{itemize}
\item Stainless Steel Swagelok Tube Fitting, Male Tube Adapter, 1/4 $''$ Tube OD x 1/4 $''$ Male NPT: SS-4-TA-1-4
\end{itemize}

\begin{itemize}
\item Stainless Steel Swagelok Tube Fitting, Male Tube Adapter, 1/4 $''$  Tube OD x 1/8$''$ Male NPT: SS-4-TA-1-2 
\end{itemize}

\begin{itemize}
\item Stainless Steel Swagelok Tube Fitting, Reducing Union Tee, 1/2 $''$  x 1/2 $''$  x 1/4 $''$ Tube OD: SS-810-3-8-4
\end{itemize}

\begin{itemize}
\item One pressure gauge. It has a range from 0 to 100 psi: PGI-63C-OG100-LAQX
\end{itemize} 
\textbf{Valves}: All valves are manufactured by Swagelok and were purchased through Edmonton Valve and Fitting. The list includes:\\
\\
\begin{itemize}
\item Two 3-way 1/2 $''$ valves:SS-45XS8: 
\end{itemize}

\begin{itemize}
\item Two 1/4 $''$valves for the drain ports on the filter housings: SS-42GS4
\end{itemize} 
\textbf{Pump, Filter, and Pulsation Dampener}\\
\\
\textbf{Air Operated Diaphragm Pump}\\
The choice to go with an pump was based on experience from similar wash systems built. Additionally, it is cost effective compared to other pumps and does not require electricity to operate. The Air Operated Double Diaphragm  pump was manufactured by Sandpiper. It has a housing made out of aluminum and stainless steel and all wetted materials are made up of stainless steel and PTFE. \\
\begin{itemize}
\item \url{https://www.sandpiperpump.com/products/standard-duty-ball/s05-metallic}
\item \url{https://www.mcmaster.com/41655k27}\\
\end{itemize}

\begin{figure}[!htpb]
  \centering
  
  \caption{Performance curve}
  \label{fig:curve}
\end{figure} 
 
The diaphragm and check valve balls are made out of PTFE and the maximum air pressure the pump can handle is 125 psi .The purchased air regulator has an air flow of 53 cfm at 100 psi and has a maximum pressure of 140 psi.\ The performance curve of the pump is shown in Figure~\ref{fig:curve} \\
 \\
 \textbf{Filter Housing}\\
To not impede the flow rate of the fluid, 20$''$ long filter housings have purchased and to accommodate the filters, two stainless steel Shelco 20$''$  Filter housings have procured through CPS Filtration. They are designed for a 20$''$ (length) and 2.5$''$  (diameter) filter cartridge.\\
\url{ https://cpsfiltration.com}\\
\\
\textbf{Filter Cartridge}\\
The cartridges are made up of 20$''$ PTFE membrane with polypropylene core material and Teflon (PTFE) gaskets.  The filter cartridges were purchased through CPS filtration and  are manufactured by American Melt Blown and Filtration. They have a maximum differential pressure of 45 psid (pounds per square inch differential).\\
\url{  https://cpsfiltration.com}\\
\\
\textbf{Pulsation Dampener}\\
One disadvantage to using an AODD pump, is that the pressure of the fluid is periodic, since the pump pulses due to the diaphragms opening and closing. The pulsation dampener is designed to correct this by “smoothing” out the pulsations of the fluid, so that a steady flow is achieved. The pulsation dampener was manufactured by Blacoh Fluid Control (\url{https://www.blacoh.com/home.aspx}) and  model CT3120T was purchased through Natpro. The pulsation dampener is made out of stainless steel with a PTFE bladder.  It holds a maximum operating pressure of 300 psi at \ang{20} C. The pulsation dampener must be charged to 80$\%$ of the head pressure to ensure maximal dampening.\\
\\
\textbf{Cart Framing}\\
Made out of 1.5” T-Slot Aluminum extrusions (manufactured by 8020) due to its ease of assembly and versatility. 
\url{https://8020.net/?SID=og9et35936f61t6v13tron8os1}
\url{https://www.mcmaster.com/47065t103}    \\
\begin{figure}[!htpb]
  \centering
  
  \caption{Aluminum cart framing}
  \label{fig:frame}
\end{figure}

\textbf{Spill Tray}
\begin{itemize}
\item Made out of polypropylene:\url{https://www.usplastic.com/catalog/item.aspx?itemid=125655}
\item Dimension: 24$''$x24$''$x4$''$
\item Can hold 37 litres of fluid\\
\end{itemize}

\section{Appendix}
Important links for Spray nozzles and related literature :\\
\\
\url{https://www.spray.ca}\\
\\
\url{https://www.spray.com/-/media/DAM/Sales-Materials/b/B652A_Spray_Technology_Dust_Control.pdf}\\
\\
\url{https://www.spray.ca/spray_nozzles/full_cone_fulljet_nozzles.aspx}\\
\\
\url{https://www.spray.ca/literature/literature_cat75.aspx}\\
\\
\url{https://www.spray.ca/Assets/SPRAY/Cat75HYD_US_B.pdf}\\
\\

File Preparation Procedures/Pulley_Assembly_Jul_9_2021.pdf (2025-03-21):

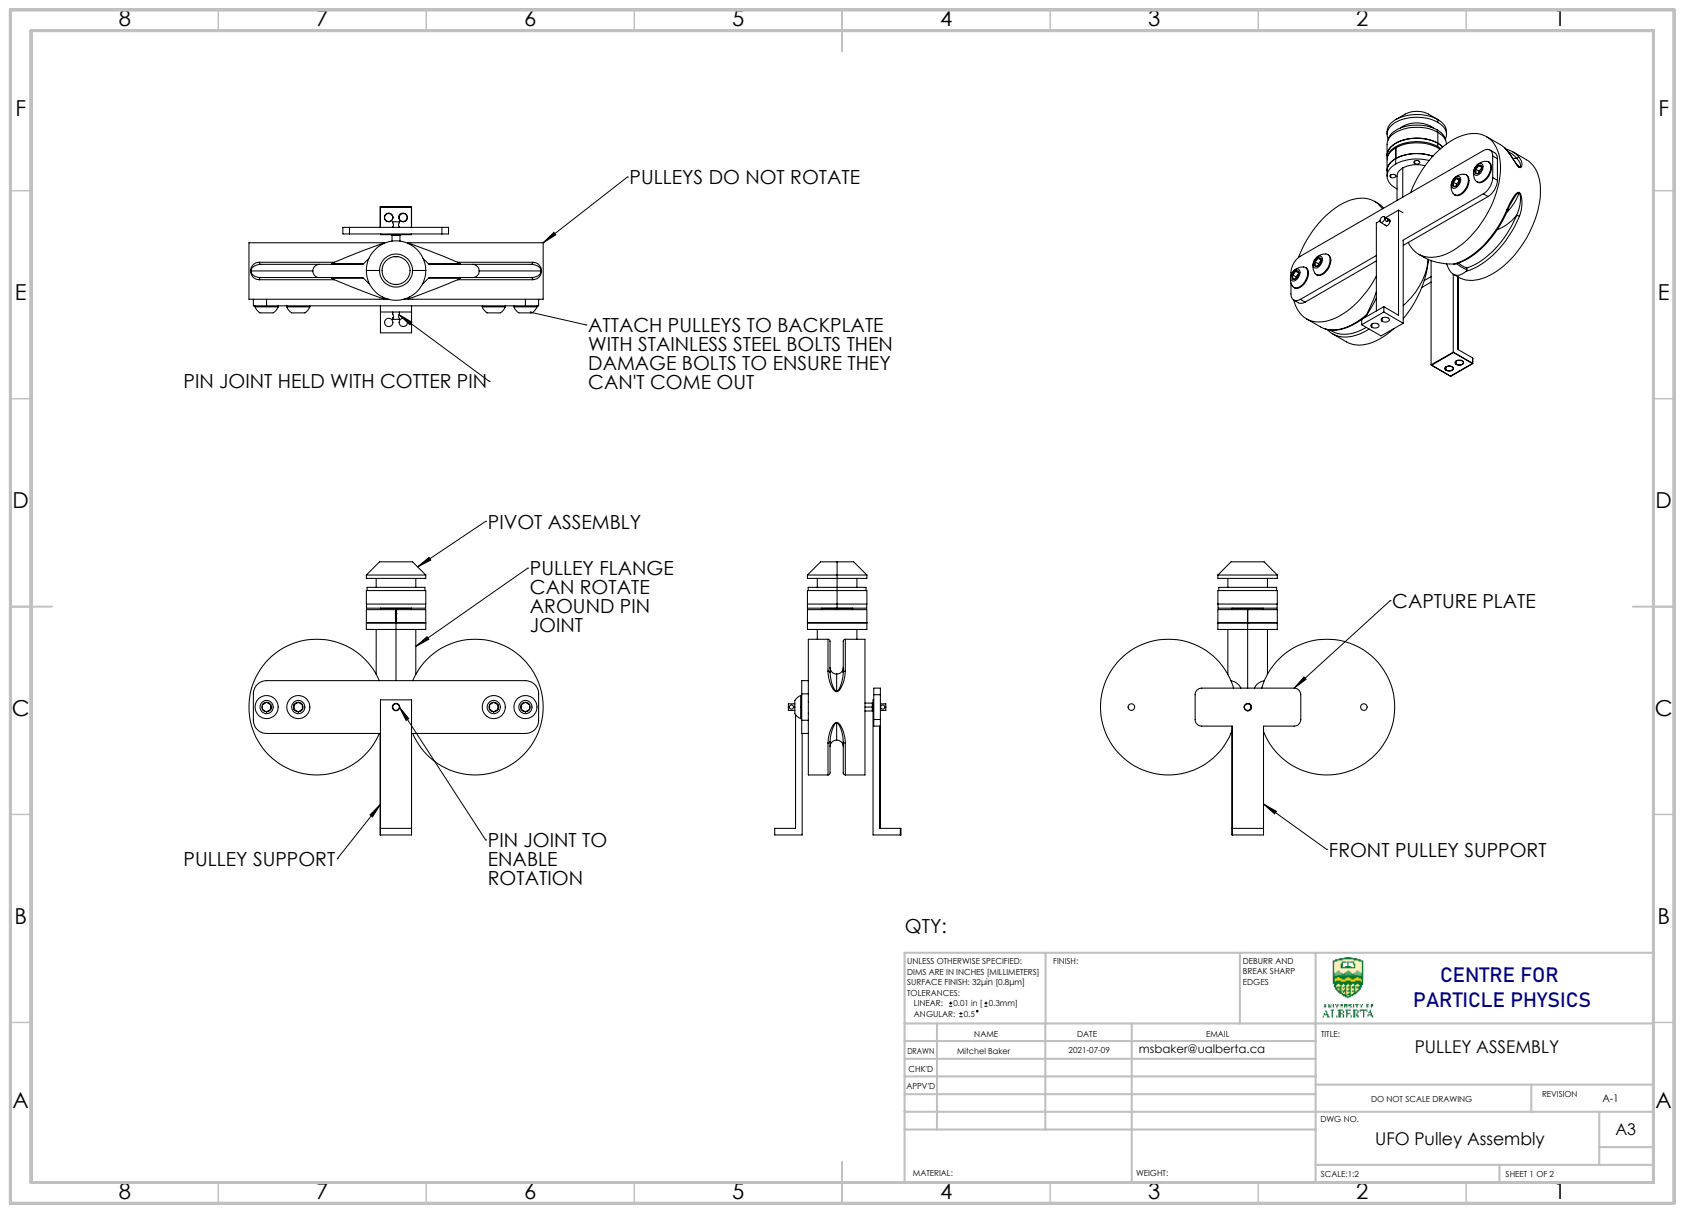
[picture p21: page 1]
PIVOT ASSEMBLY; PULLEY FLANGE CAN ROTATE AROUND PIN; PULLEY SUPPORT; CAPTURE PLATE

PULLEYS DO NOT ROTATE

ATTACH PULLEYS TO BACKPLATE
WITH STAINLESS STEEL BOLTS THEN
DAMAGE BOLTS TO ENSURE THEY
CAN'T COME OUT

PIN JOINT HELD WITH COTTER PIN

PIN JOINT TO
ENABLE
ROTATION

FRONT PULLEY SUPPORT

UNLESS OTHERWISE SPECIFIED: DIMS ARE IN INCHES [MILLIMETERS] SURFACE FINISH: 32μin [0.8μm] TOLERANCES: LINEAR: 0.01 in [ 0.3mm] ANGULAR: 0.5 | FINISH: | DEBURR AND BREAK SHARP EDGES | CENTRE FOR PARTICLE PHYSICS

NAME | DATE | EMAIL | TITLE: PULLEY ASSEMBLY

DRAWN | Mitchel Baker | 2021-07-09 | msbaker@ualberta.ca

CHK'D
APPV'D

DO NOT SCALE DRAWING | REVISION A-1

DWG NO. UFO Pulley Assembly | A3

MATERIAL: | WEIGHT:

SCALE:1:2 | SHEET 1 OF 2

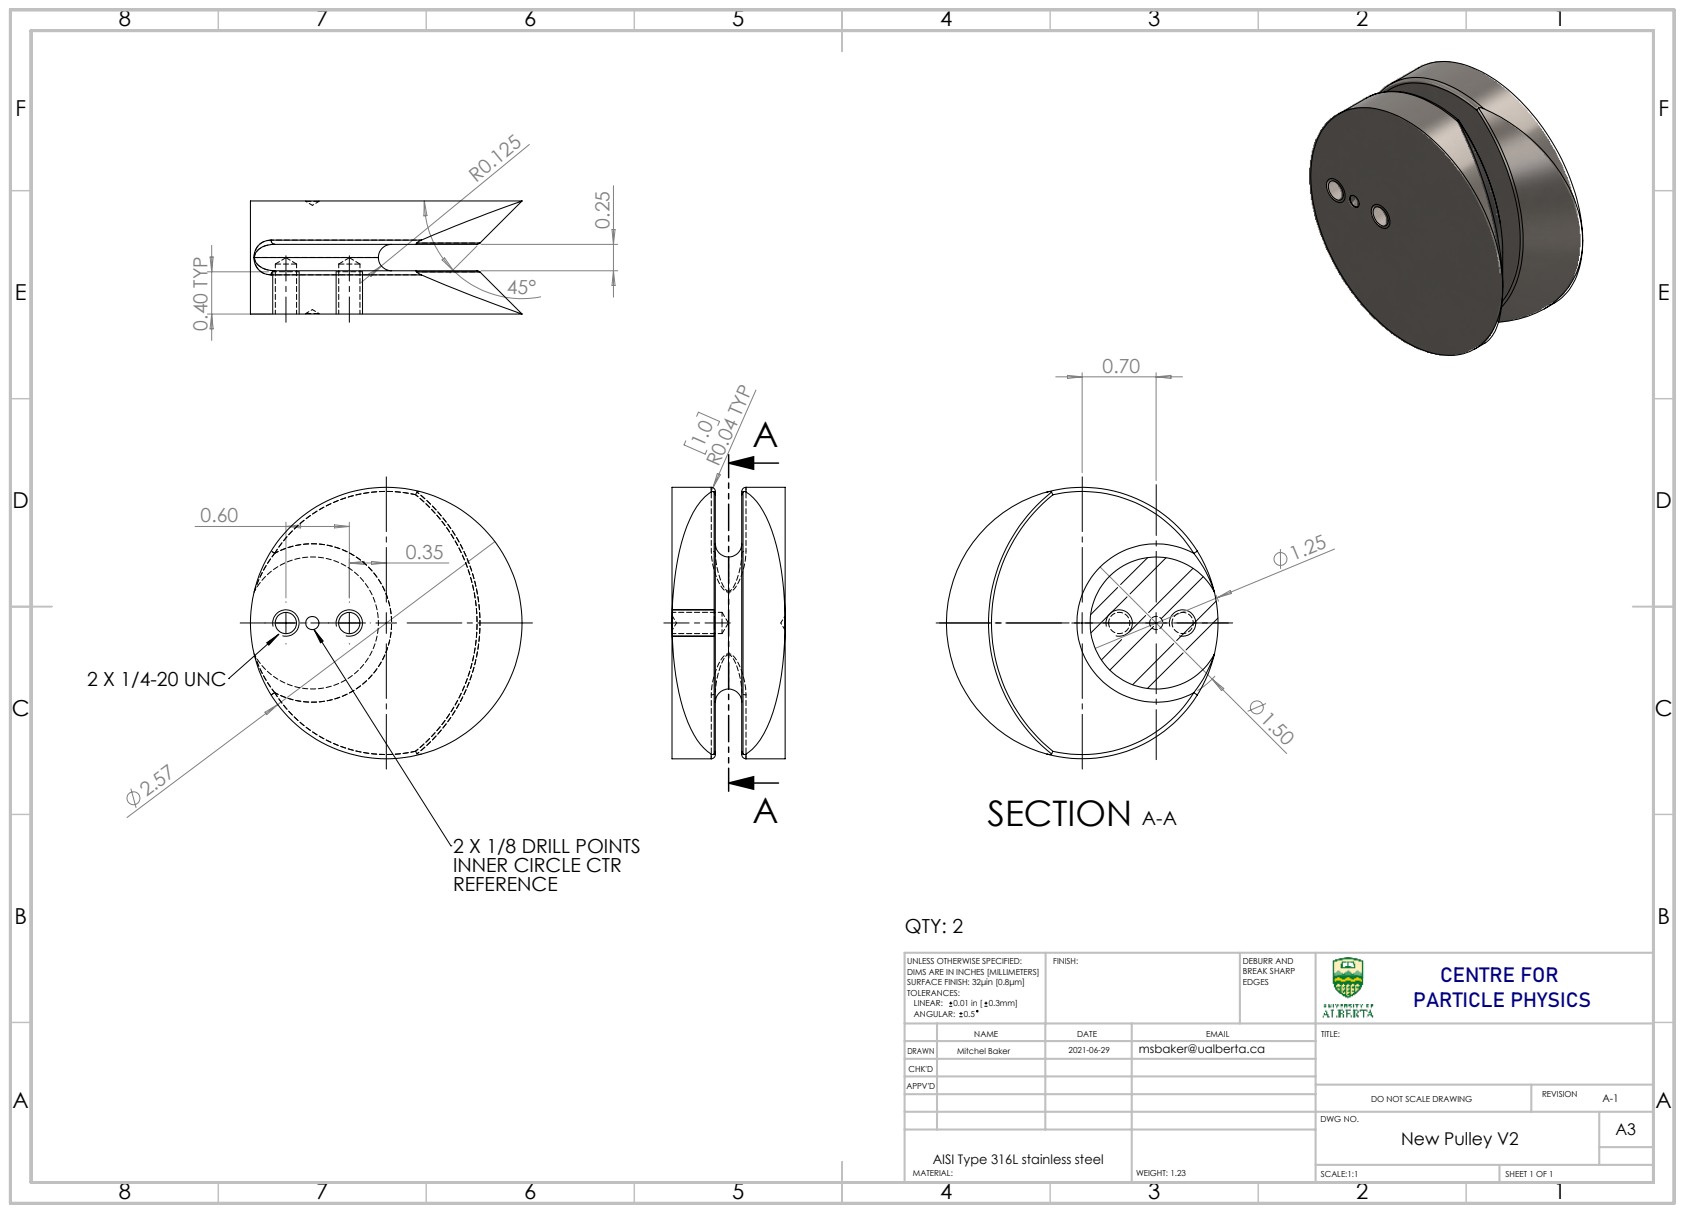
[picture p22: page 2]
2 X 1/4-20 UNC; 0.40 TYP; R0.04 TYP; SECTION A-A; QTY: 2

2 X 1/8 DRILL POINTS
INNER CIRCLE CTR
REFERENCE

UNLESS OTHERWISE SPECIFIED: DIMS ARE IN INCHES [MILLIMETERS] SURFACE FINISH: 32μin [0.8μm] TOLERANCES: LINEAR: 0.01 in [ 0.3mm] ANGULAR: 0.5 | FINISH: | DEBURR AND BREAK SHARP EDGES | CENTRE FOR PARTICLE PHYSICS

NAME | DATE | EMAIL | TITLE:

DRAWN | Mitchel Baker | 2021-06-29 | msbaker@ualberta.ca

CHK'D
APPV'D

DO NOT SCALE DRAWING | REVISION A-1

DWG NO. New Pulley V2 | A3

AISI Type 316L stainless steel MATERIAL: | WEIGHT: 1.23

SCALE:1:1 | SHEET 1 OF 1

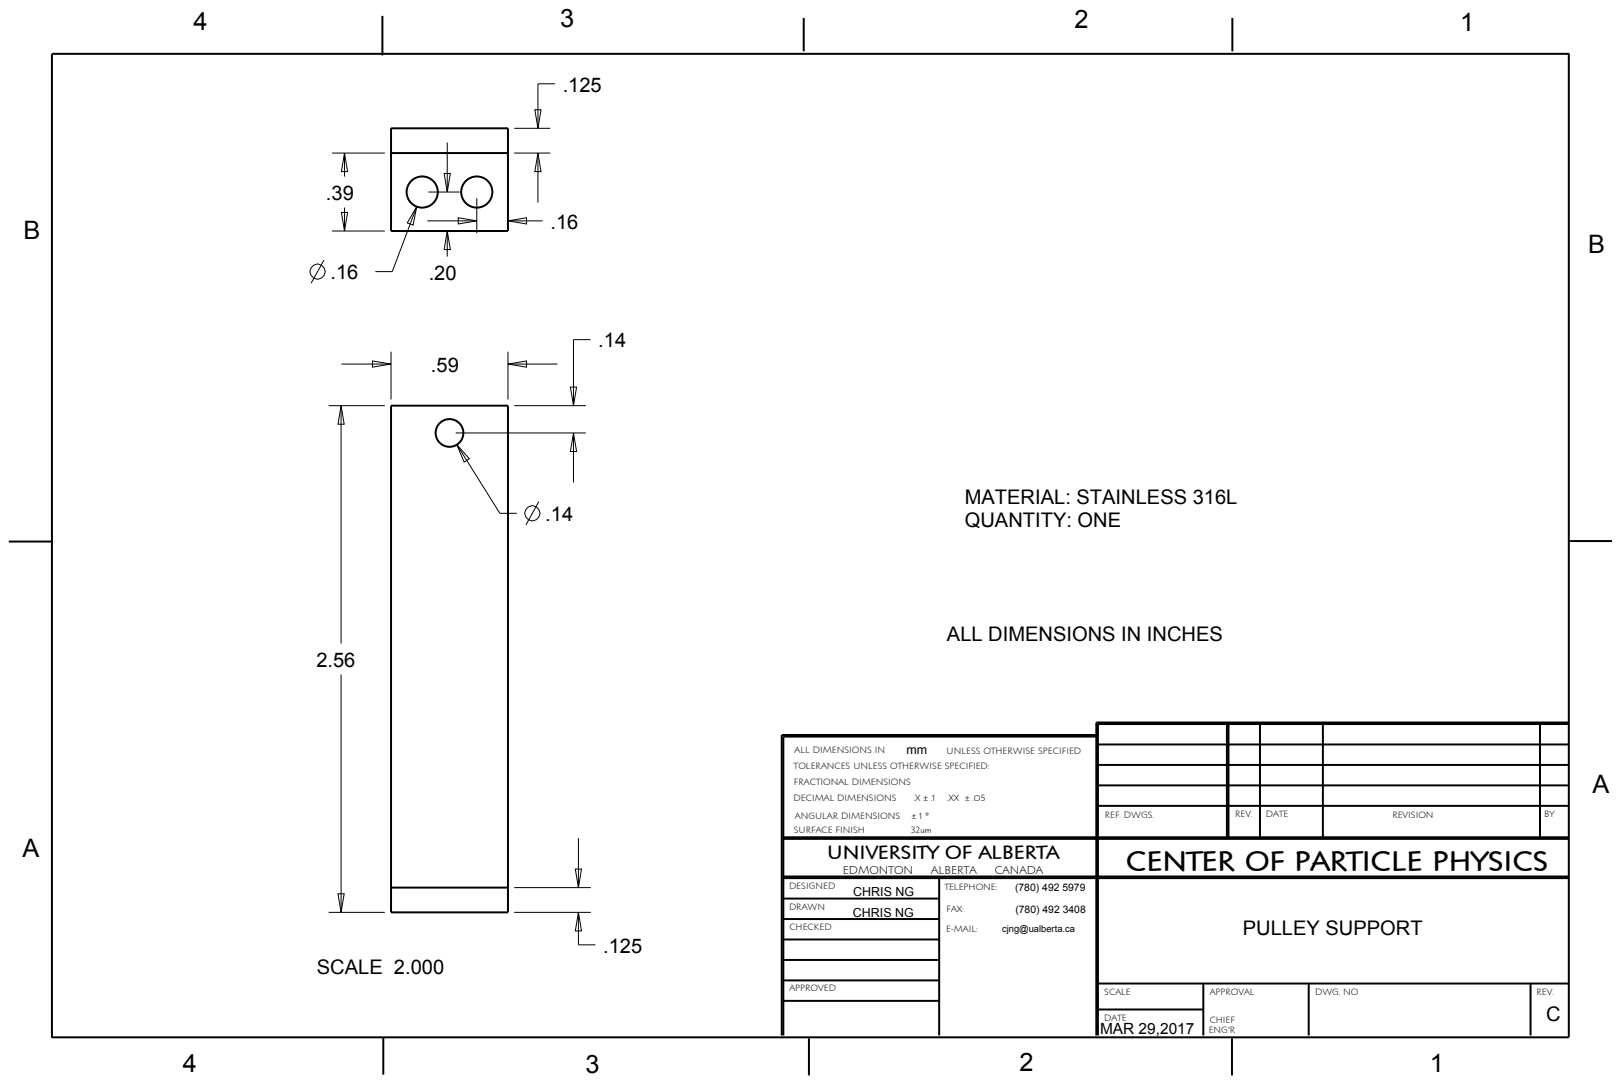
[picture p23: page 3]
DWG. NO; REV.; DECIMAL DIMENSIONS; SURFACE FINISH; CHRIS NG; MAR 29,2017; MATERIAL: STAINLESS 316L QUANTITY: ONE; SCALE 2.000

ALL DIMENSIONS IN INCHES

ALL DIMENSIONS IN
TOLERANCES UNLESS OTHERWISE SPECIFIED:
FRACTIONAL DIMENSIONS
ANGULAR DIMENSIONS ± 1 °

mm UNLESS OTHERWISE SPECIFIED

REF. DWGS. | REV. | DATE | REVISION | BY

UNIVERSITY OF ALBERTA EDMONTON ALBERTA CANADA | CENTER OF PARTICLE PHYSICS

DESIGNED CHRIS NG | TELEPHONE: (780) 492 5979 FAX: (780) 492 3408 E-MAIL: cjng@ualberta.ca | PULLEY SUPPORT

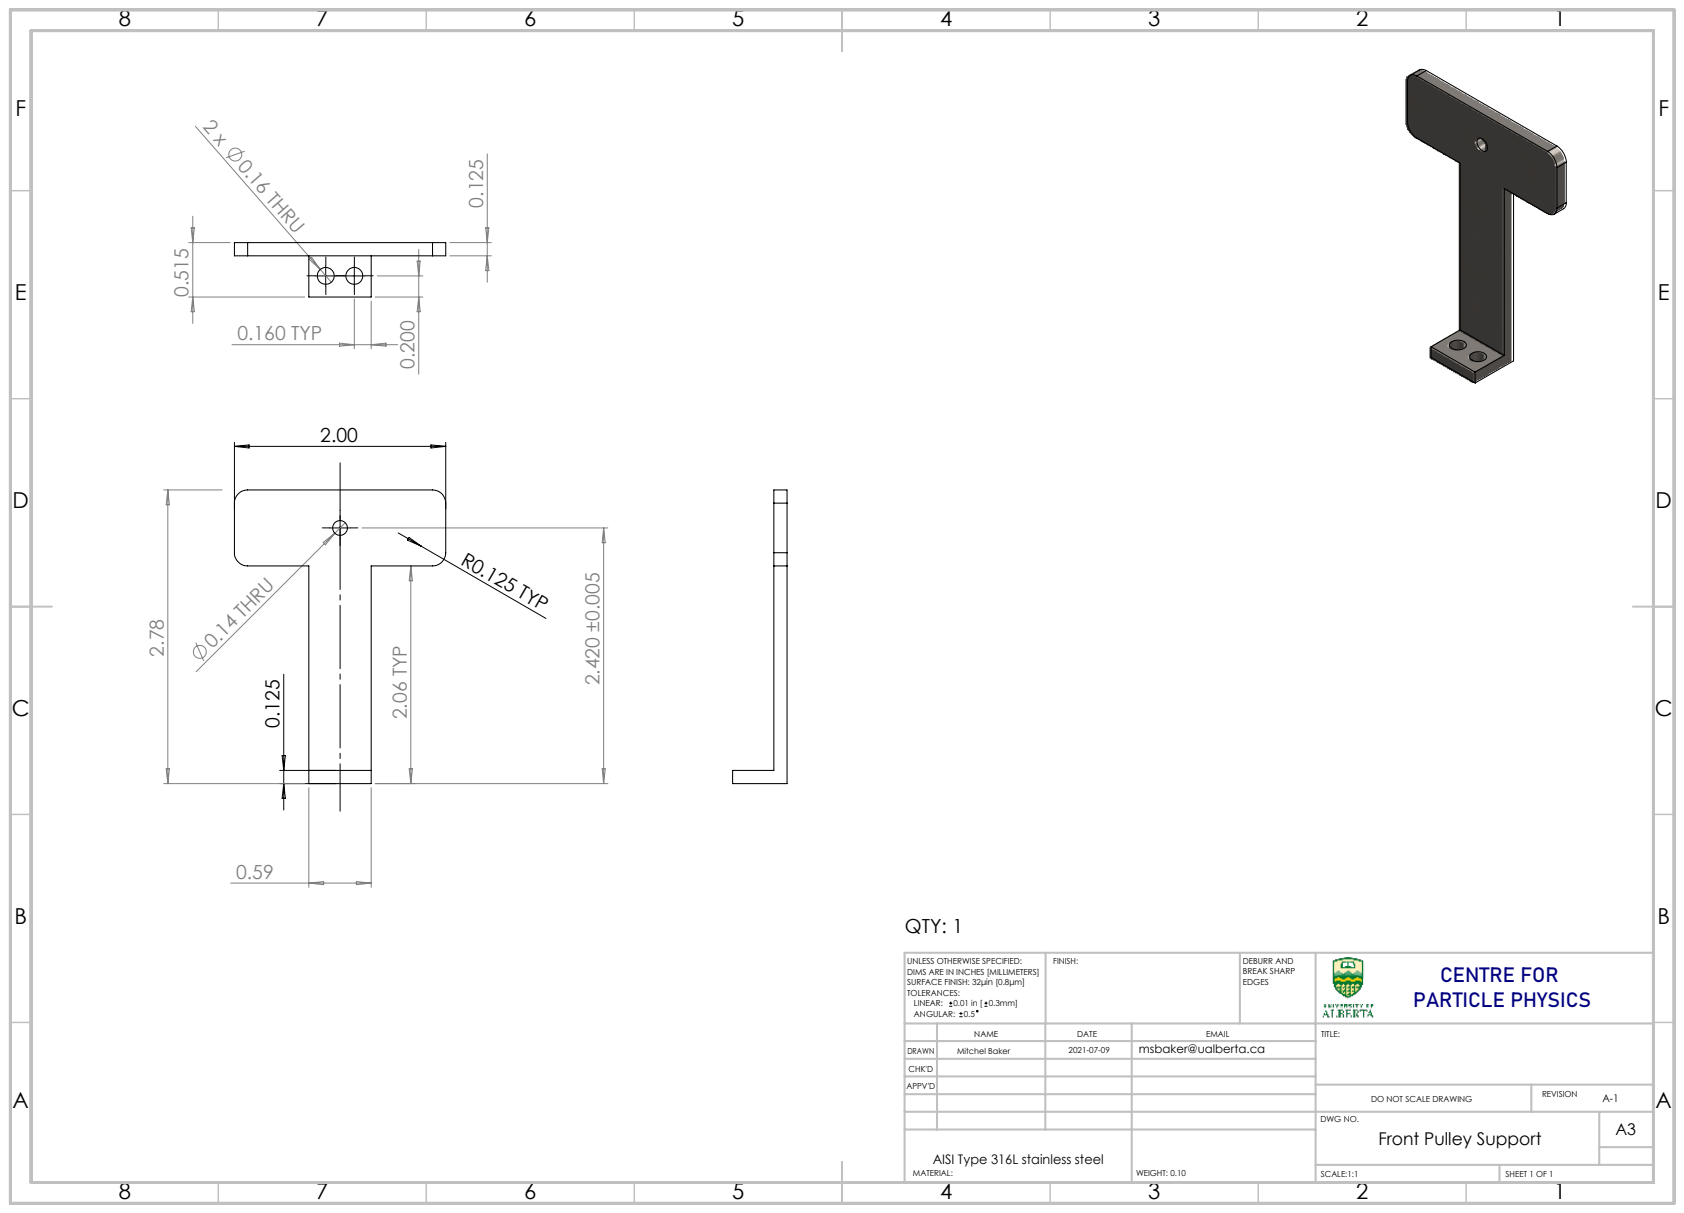
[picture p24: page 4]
R0.125 TYP; 0.14 THRU; 2.06 TYP; 0.160 TYP; 0.16 THRU; QTY: 1

UNLESS OTHERWISE SPECIFIED: DIMS ARE IN INCHES [MILLIMETERS] SURFACE FINISH: 32μin [0.8μm] TOLERANCES: LINEAR: 0.01 in [ 0.3mm] ANGULAR: 0.5 | FINISH: | DEBURR AND BREAK SHARP EDGES | CENTRE FOR PARTICLE PHYSICS

NAME | DATE | EMAIL | TITLE:

DRAWN | Mitchel Baker | 2021-07-09 | msbaker@ualberta.ca

CHK'D
APPV'D

DO NOT SCALE DRAWING | REVISION A-1

DWG NO. Front Pulley Support | A3

AISI Type 316L stainless steel MATERIAL: | WEIGHT: 0.10

SCALE:1:1 | SHEET 1 OF 1

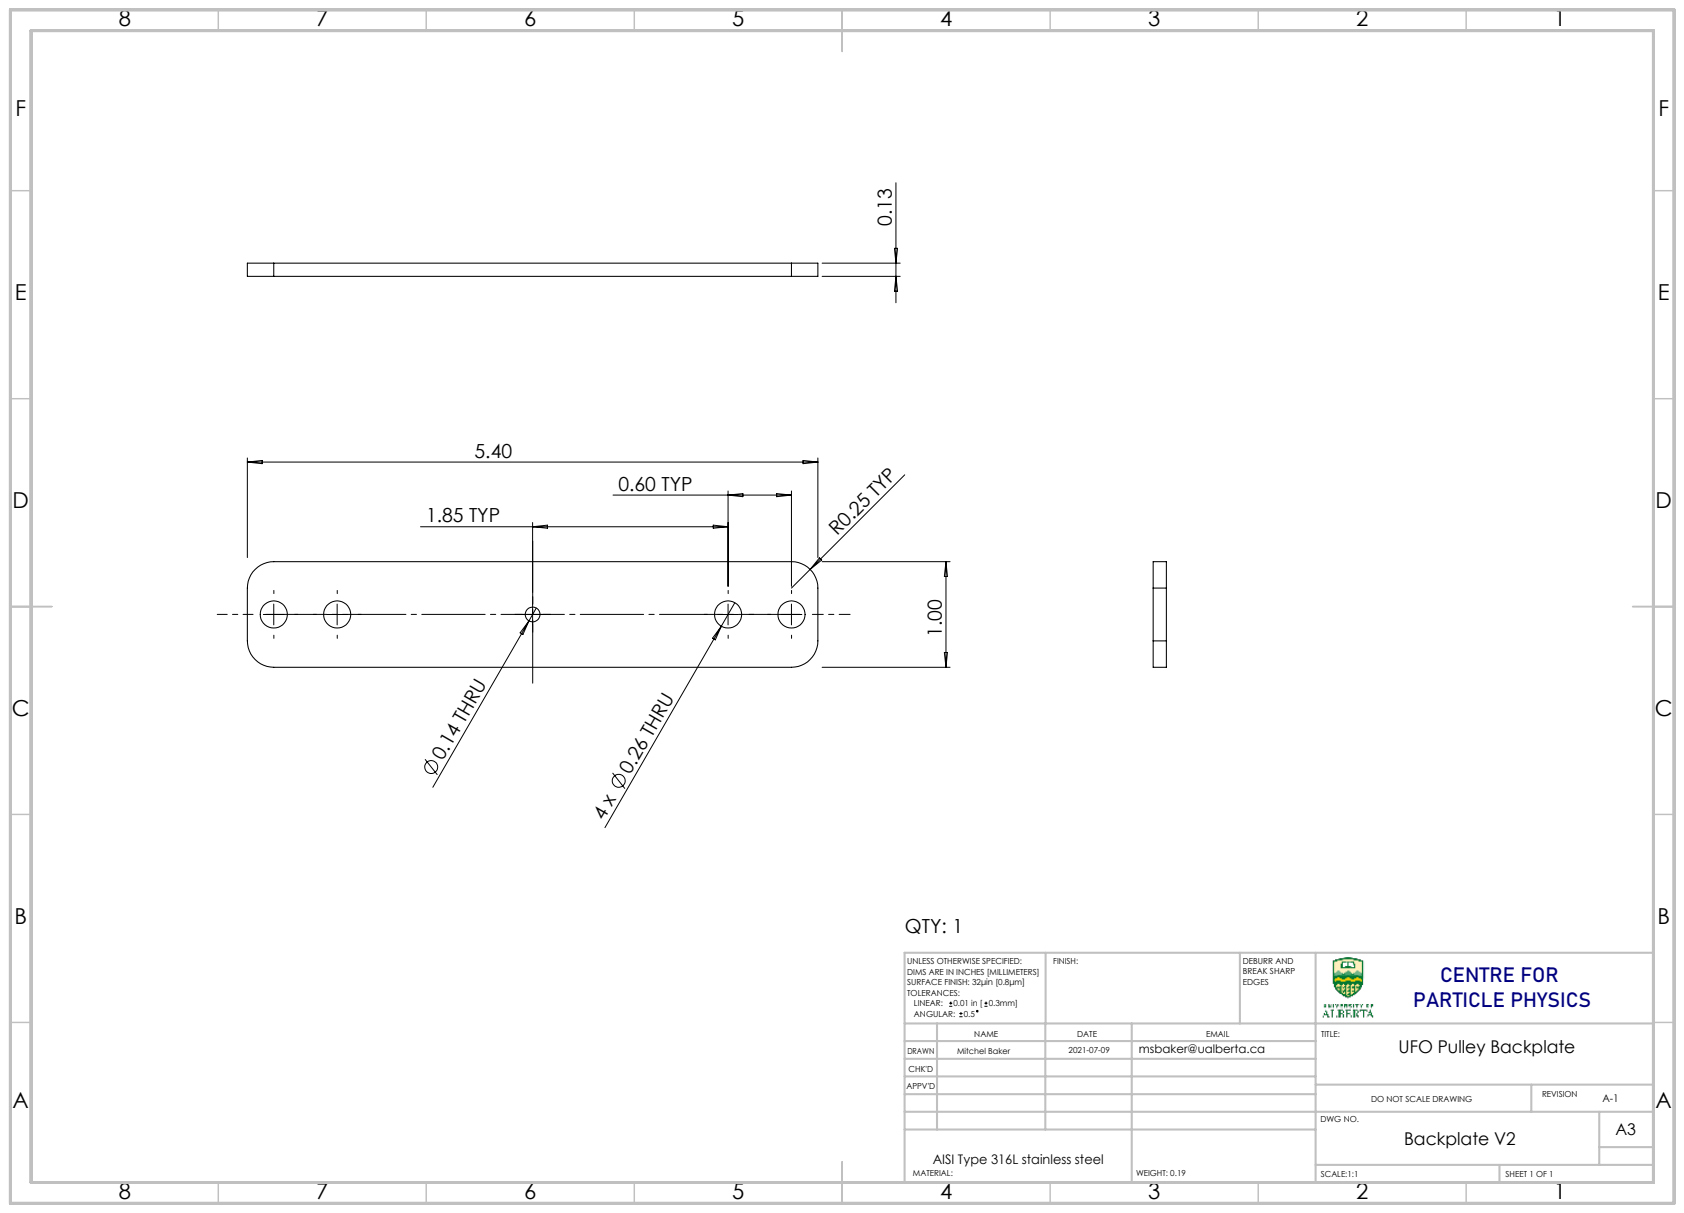
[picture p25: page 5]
0.14 THRU; 0.26 THRU; 1.85 TYP; 0.60 TYP; R0.25 TYP 0.13; QTY: 1

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

NAME | DATE | EMAIL | TITLE: UFO Pulley Backplate

DRAWN | Mitchel Baker | 2021-07-09 | msbaker@ualberta.ca

CHK'D
APPV'D

DO NOT SCALE DRAWING | REVISION A-1

DWG NO. Backplate V2 | A3

AISI Type 316L stainless steel MATERIAL: | WEIGHT: 0.19

SCALE:1:1 | SHEET 1 OF 1

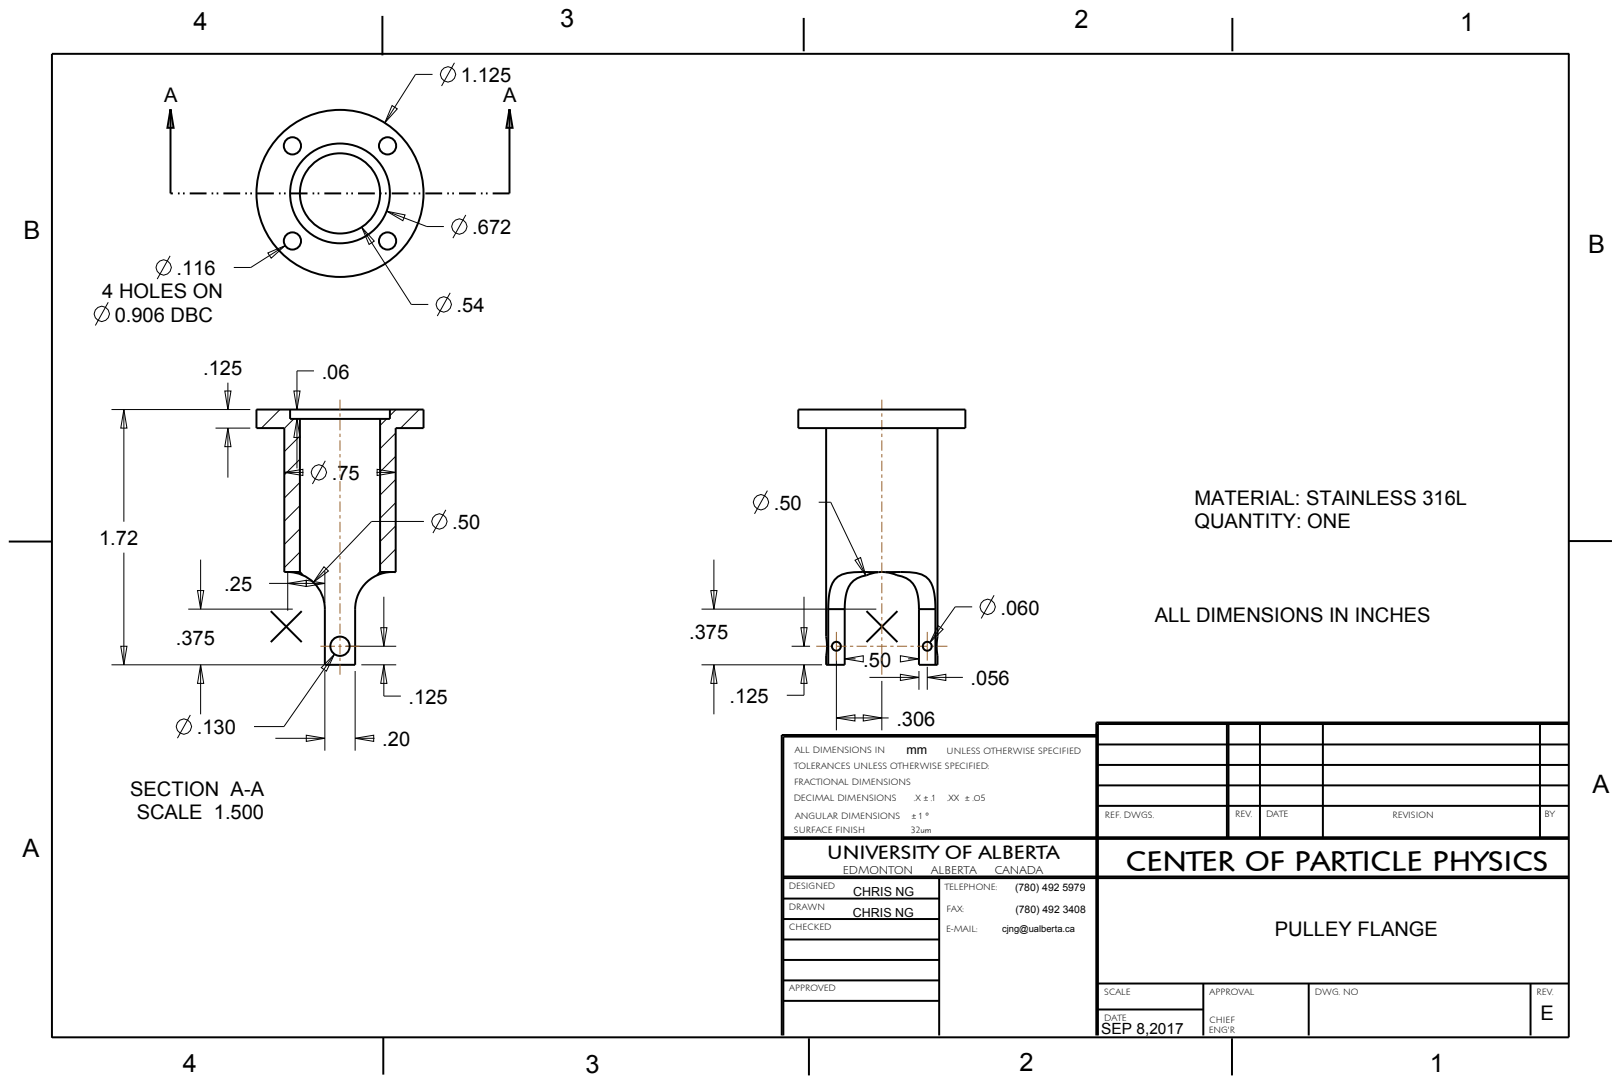
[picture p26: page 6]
DECIMAL DIMENSIONS; SURFACE FINISH; CHRIS NG; 4 HOLES ON 0.906 DBC; MATERIAL: STAINLESS 316L QUANTITY: ONE; SEP 8,2017; SCALE 1.500; SECTION A-A

ALL DIMENSIONS IN INCHES

ALL DIMENSIONS IN
TOLERANCES UNLESS OTHERWISE SPECIFIED:
FRACTIONAL DIMENSIONS
ANGULAR DIMENSIONS ± 1 °

mm UNLESS OTHERWISE SPECIFIED

REF. DWGS. | REV. | DATE | REVISION | BY

UNIVERSITY OF ALBERTA EDMONTON ALBERTA CANADA | CENTER OF PARTICLE PHYSICS

DESIGNED CHRIS NG | TELEPHONE: (780) 492 5979 FAX: (780) 492 3408 E-MAIL: cjng@ualberta.ca | PULLEY FLANGE

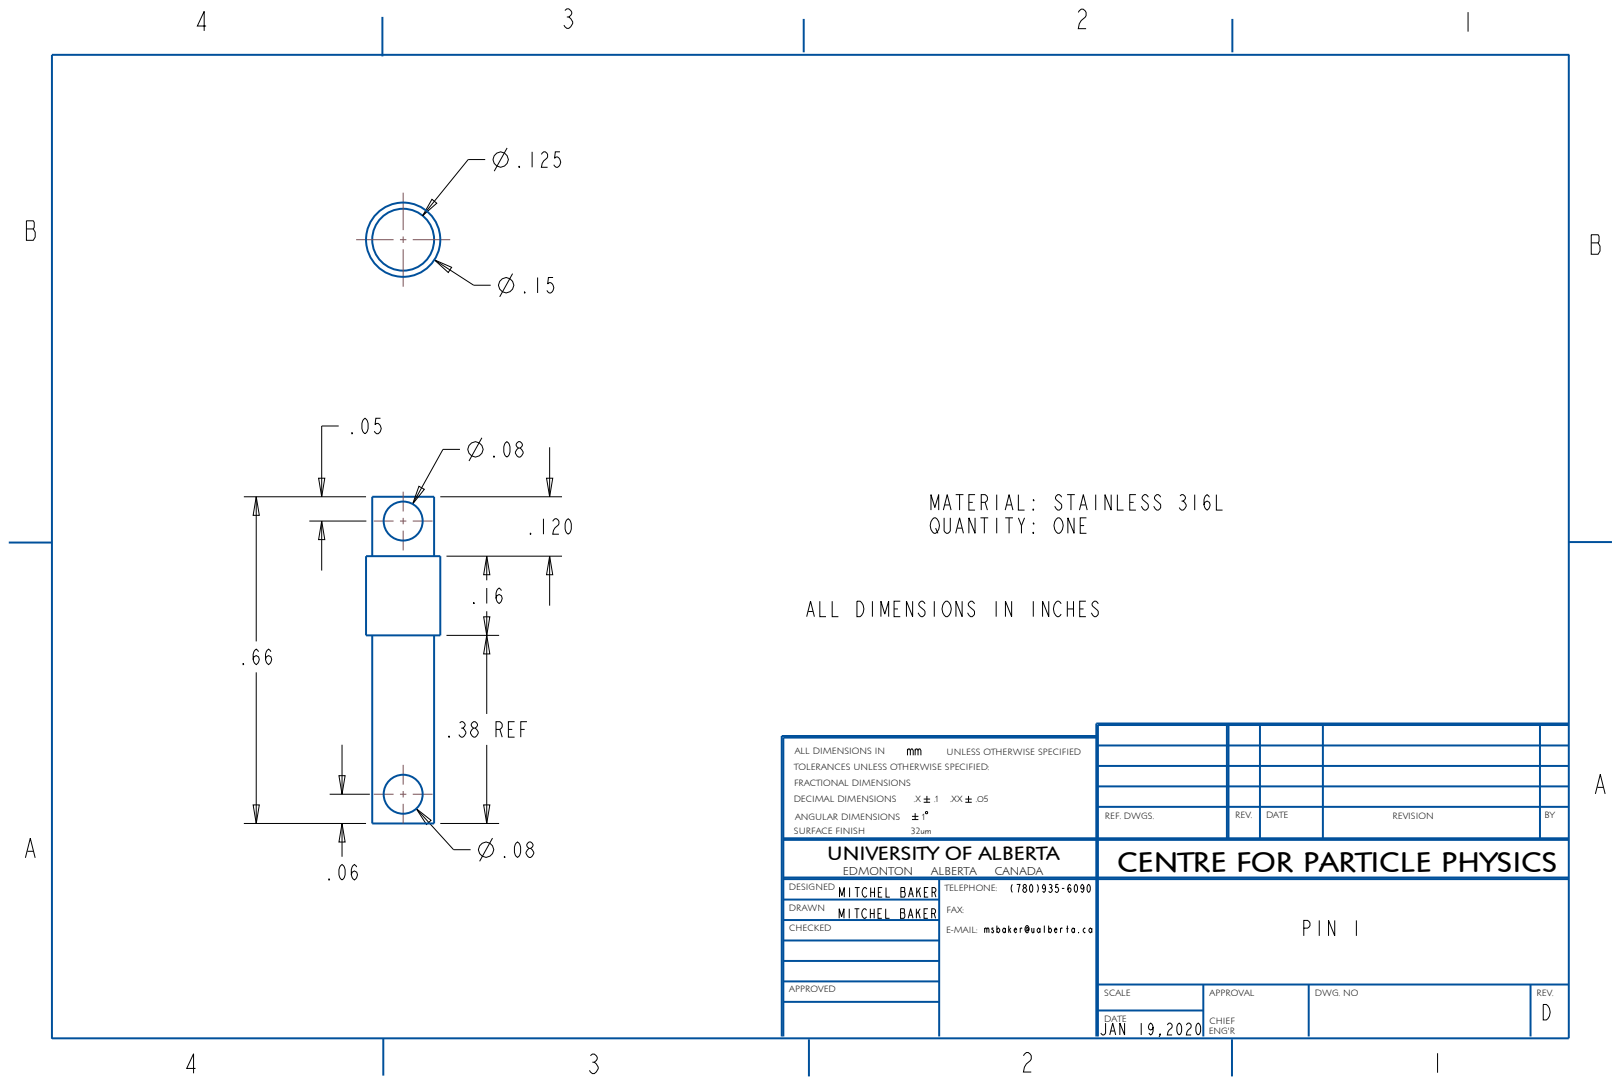
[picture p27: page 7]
.38 REF; MATERIAL: STAINLESS 316L QUANTITY: ONE; JAN 19,2020; DECIMAL DIMENSIONS; ANGULAR DIMENSIONS; SURFACE FINISH

ALL DIMENSIONS IN INCHES

ALL DIMENSIONS IN
TOLERANCES UNLESS OTHERWISE SPECIFIED:
FRACTIONAL DIMENSIONS

UNLESS OTHERWISE SPECIFIED

REF. DWGS. | REV. | DATE | REVISION | BY

UNIVERSITY OF ALBERTA EDMONTON ALBERTA CANADA | CENTRE FOR PARTICLE PHYSICS
MITCHEL BAKER | | | | | TELEPHONE: (780)935-6090 FAX: msbaker@ualberta.ca | PIN 1
MITCHEL BAKER

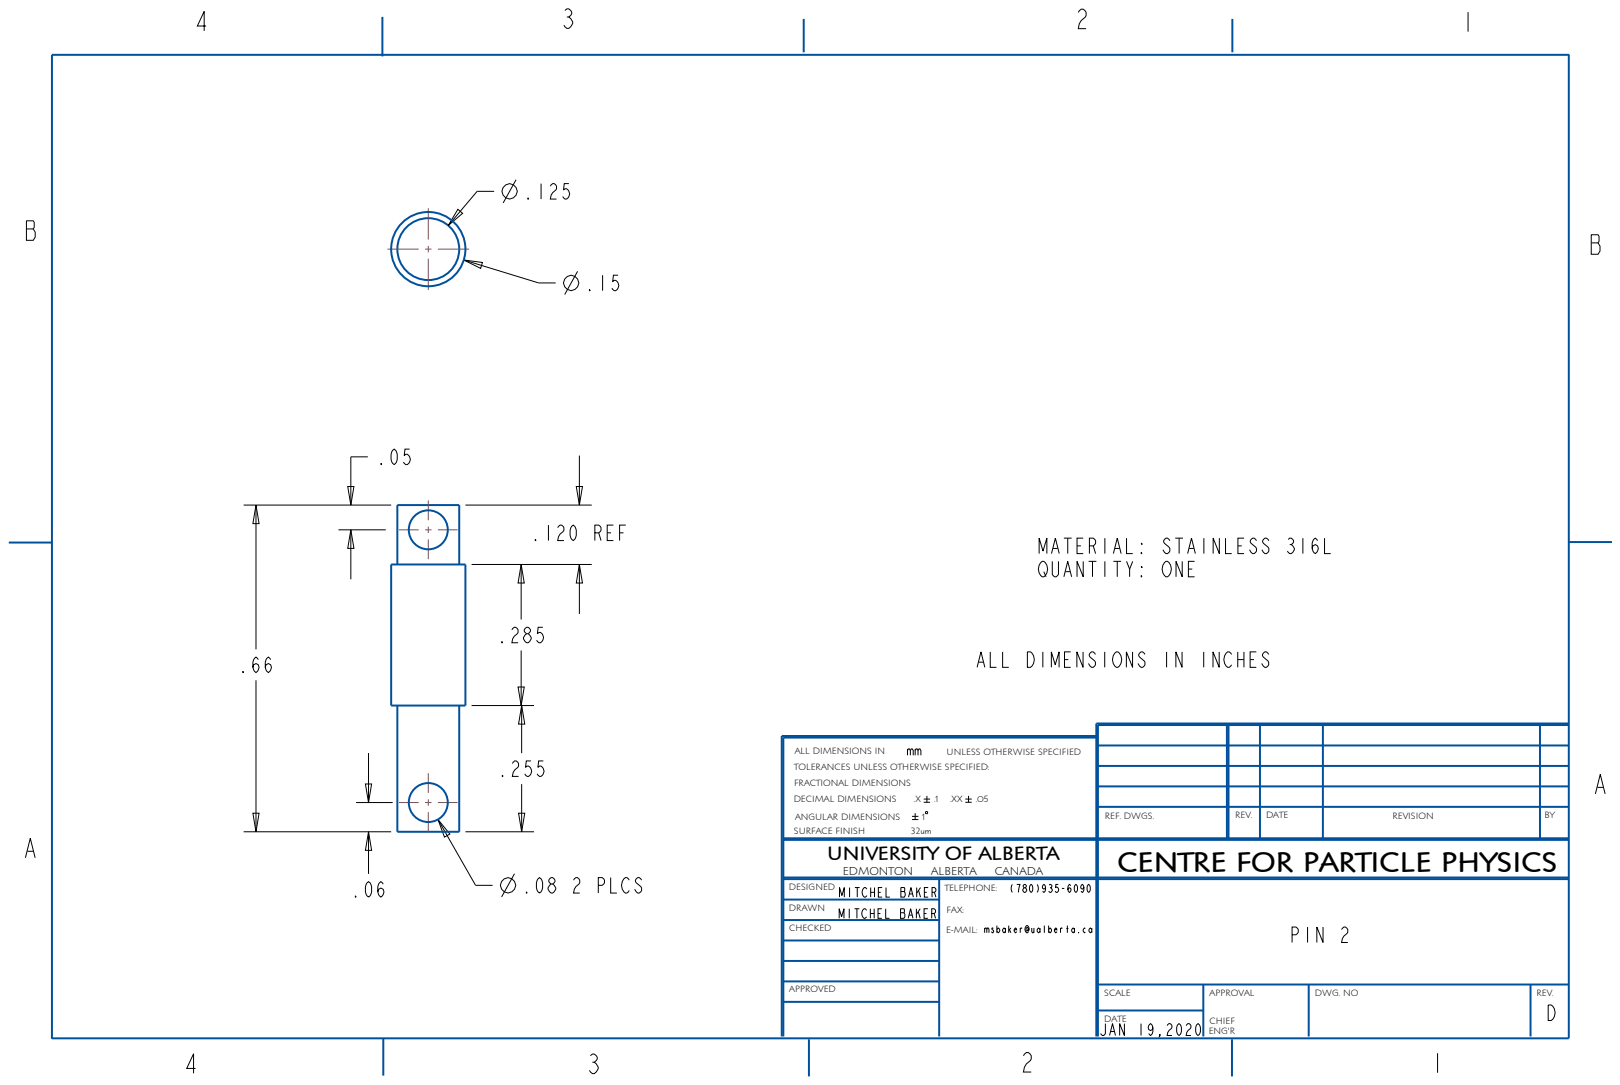
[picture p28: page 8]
.08 2 PLCS; .120 REF; MATERIAL: STAINLESS 316L QUANTITY: ONE; JAN 19,2020; DECIMAL DIMENSIONS; ANGULAR DIMENSIONS; SURFACE FINISH

ALL DIMENSIONS IN INCHES

ALL DIMENSIONS IN
TOLERANCES UNLESS OTHERWISE SPECIFIED:
FRACTIONAL DIMENSIONS

UNLESS OTHERWISE SPECIFIED

REF. DWGS. | REV. | DATE | REVISION | BY

UNIVERSITY OF ALBERTA EDMONTON ALBERTA CANADA | CENTRE FOR PARTICLE PHYSICS
MITCHEL BAKER | | | | | TELEPHONE: (780)935-6090 FAX: msbaker@ualberta.ca | PIN 2
MITCHEL BAKER

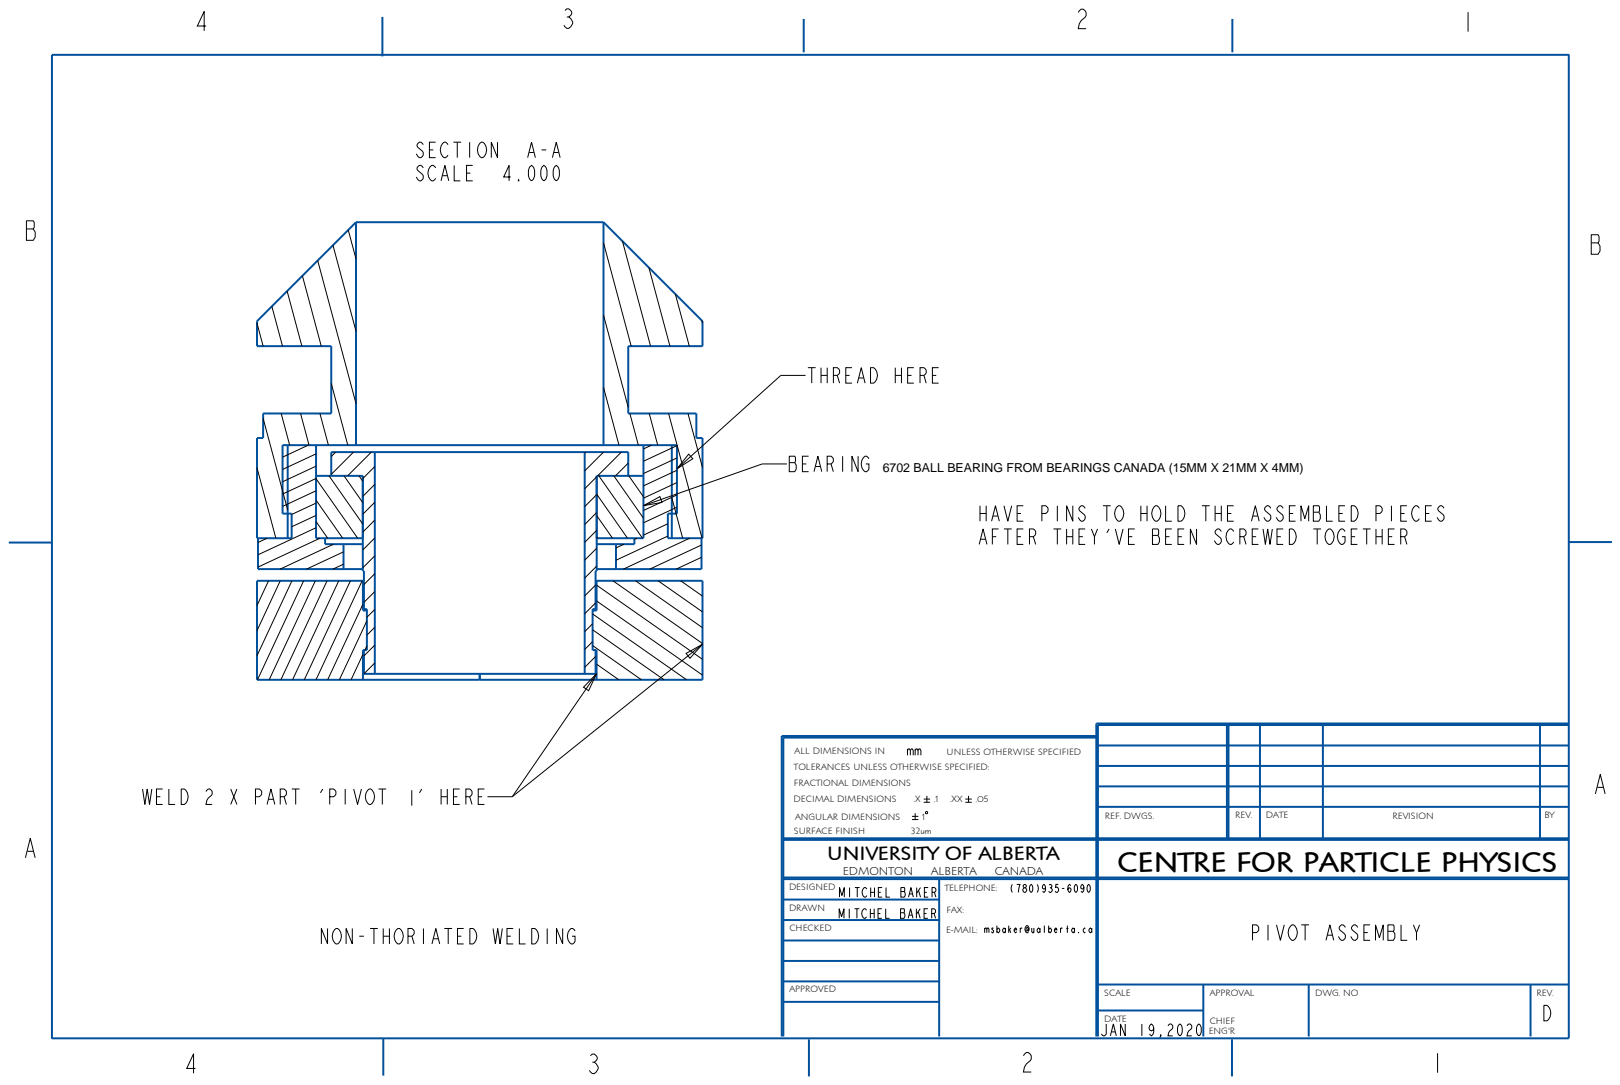
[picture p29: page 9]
MITCHEL BAKER MITCHEL BAKER; HAVE PINS; HOLD THE ASSEMBLED PIECES; AFTER; THEY'VE BEEN SCREWED TOGETHER; SECTION A-A SCALE 4.000; BEARI fdNG; DECIMAL DIMENSIONS; ANGULAR DIMENSIONS; SURFACE FINISH

6702 BALL BEARING FROM BEARINGS CANADA (15MM X 21MM X 4MM)

ALL DIMENSIONS IN
TOLERANCES UNLESS OTHERWISE SPECIFIED:
FRACTIONAL DIMENSIONS

UNLESS OTHERWISE SPECIFIED

WELD 2 X PART 'PIVOT 2' HERE

REF. DWGS. | REV. | DATE | REVISION | BY

UNIVERSITY OF ALBERTA EDMONTON ALBERTA CANADA | CENTRE FOR PARTICLE PHYSICS

TELEPHONE: FAX: msbaker@ualberta.ca | | (780)935-6090 | | PIVOT ASSEMBLY

NON-THORIATED WELDING

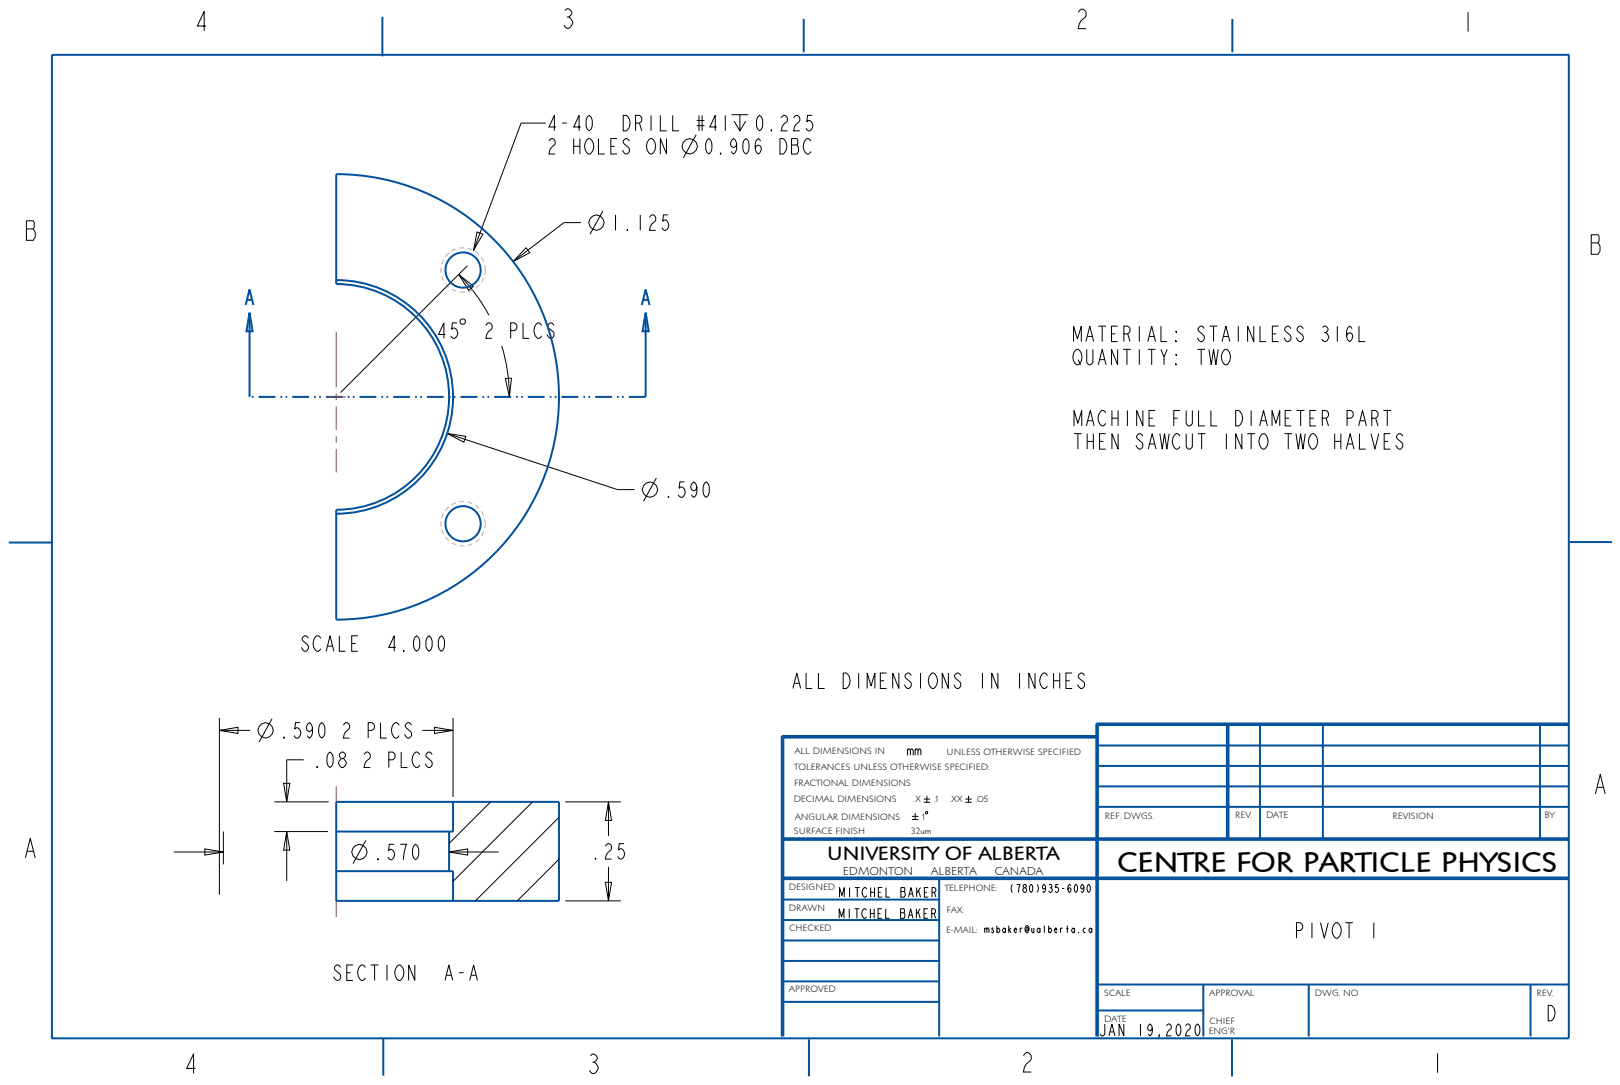
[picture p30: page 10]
MITCHEL BAKER; 45 2 PLCS; .590 2 PLCS .08 2 PLCS; JAN 19,2020; MACHINE FULL; DIAMETER PART; SCALE 4.000; 4-40 DRILL; SECTION A-A; DECIMAL DIMENSIONS; ANGULAR DIMENSIONS; SURFACE FINISH

2 HOLES ON 0.906 DBC

MATERIAL: STAINLESS 316L
QUANTITY: TWO
THEN SAWCUT INTO TWO HALVES

ALL DIMENSIONS IN INCHES

ALL DIMENSIONS IN
TOLERANCES UNLESS OTHERWISE SPECIFIED:
FRACTIONAL DIMENSIONS

UNLESS OTHERWISE SPECIFIED

REF. DWGS. | REV. | DATE | REVISION | BY

UNIVERSITY OF ALBERTA EDMONTON ALBERTA CANADA | CENTRE FOR PARTICLE PHYSICS
MITCHEL BAKER | | | | | TELEPHONE: (780)935-6090 FAX: msbaker@ualberta.ca | PIVOT 1

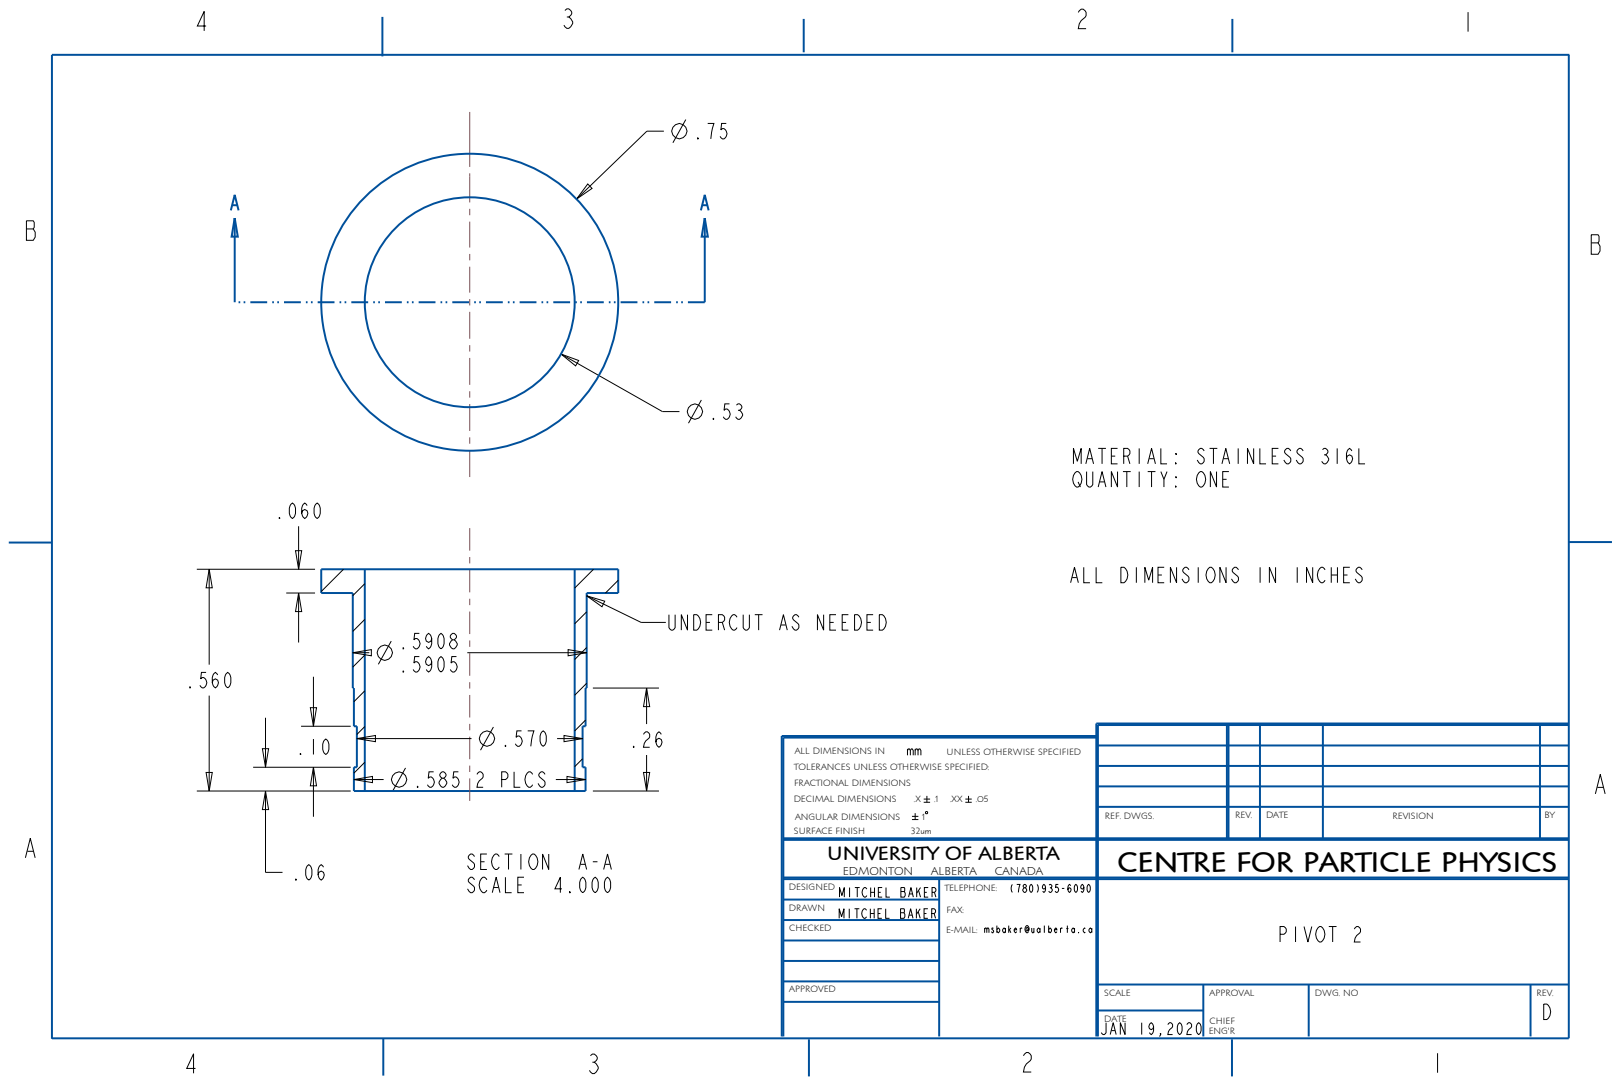
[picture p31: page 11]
2 PLCS; MATERIAL: STAINLESS 316L QUANTITY: ONE; JAN 19,2020; SECTION A-A SCALE 4.000; DECIMAL DIMENSIONS; ANGULAR DIMENSIONS; SURFACE FINISH

ALL DIMENSIONS IN INCHES

UNDERCUT AS NEEDED

ALL DIMENSIONS IN
TOLERANCES UNLESS OTHERWISE SPECIFIED:
FRACTIONAL DIMENSIONS

UNLESS OTHERWISE SPECIFIED

REF. DWGS. | REV. | DATE | REVISION | BY

UNIVERSITY OF ALBERTA EDMONTON ALBERTA CANADA | CENTRE FOR PARTICLE PHYSICS
MITCHEL BAKER | | | | | TELEPHONE: (780)935-6090 FAX: msbaker@ualberta.ca | PIVOT 2
MITCHEL BAKER

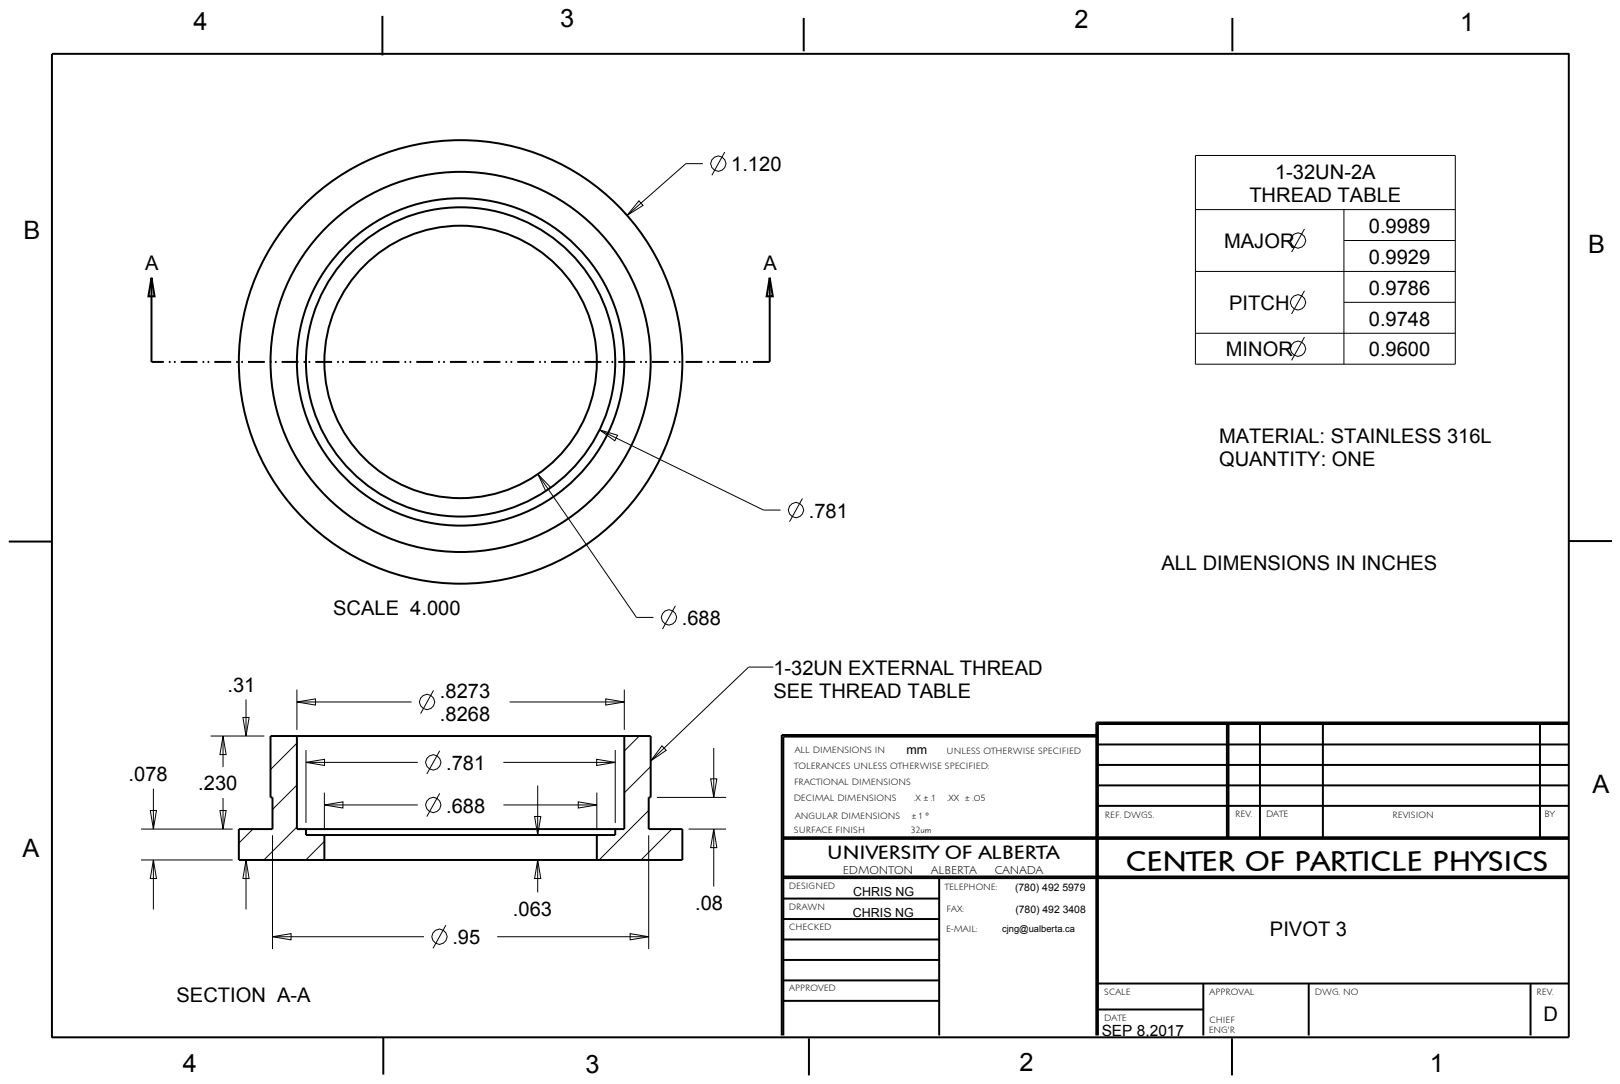
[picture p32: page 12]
DECIMAL DIMENSIONS; SURFACE FINISH; CHRIS NG; THREAD TABLE; MATERIAL: STAINLESS 316L QUANTITY: ONE; SEP 8,2017; SCALE 4.000; SECTION A-A

ALL DIMENSIONS IN INCHES

1-32UN EXTERNAL THREAD
SEE THREAD TABLE

ALL DIMENSIONS IN
TOLERANCES UNLESS OTHERWISE SPECIFIED:
FRACTIONAL DIMENSIONS
ANGULAR DIMENSIONS ± 1 °

mm UNLESS OTHERWISE SPECIFIED

REF. DWGS. | REV. | DATE | REVISION | BY

UNIVERSITY OF ALBERTA EDMONTON ALBERTA CANADA | CENTER OF PARTICLE PHYSICS

DESIGNED CHRIS NG | TELEPHONE: (780) 492 5979 FAX: (780) 492 3408 E-MAIL: cjng@ualberta.ca | PIVOT 3

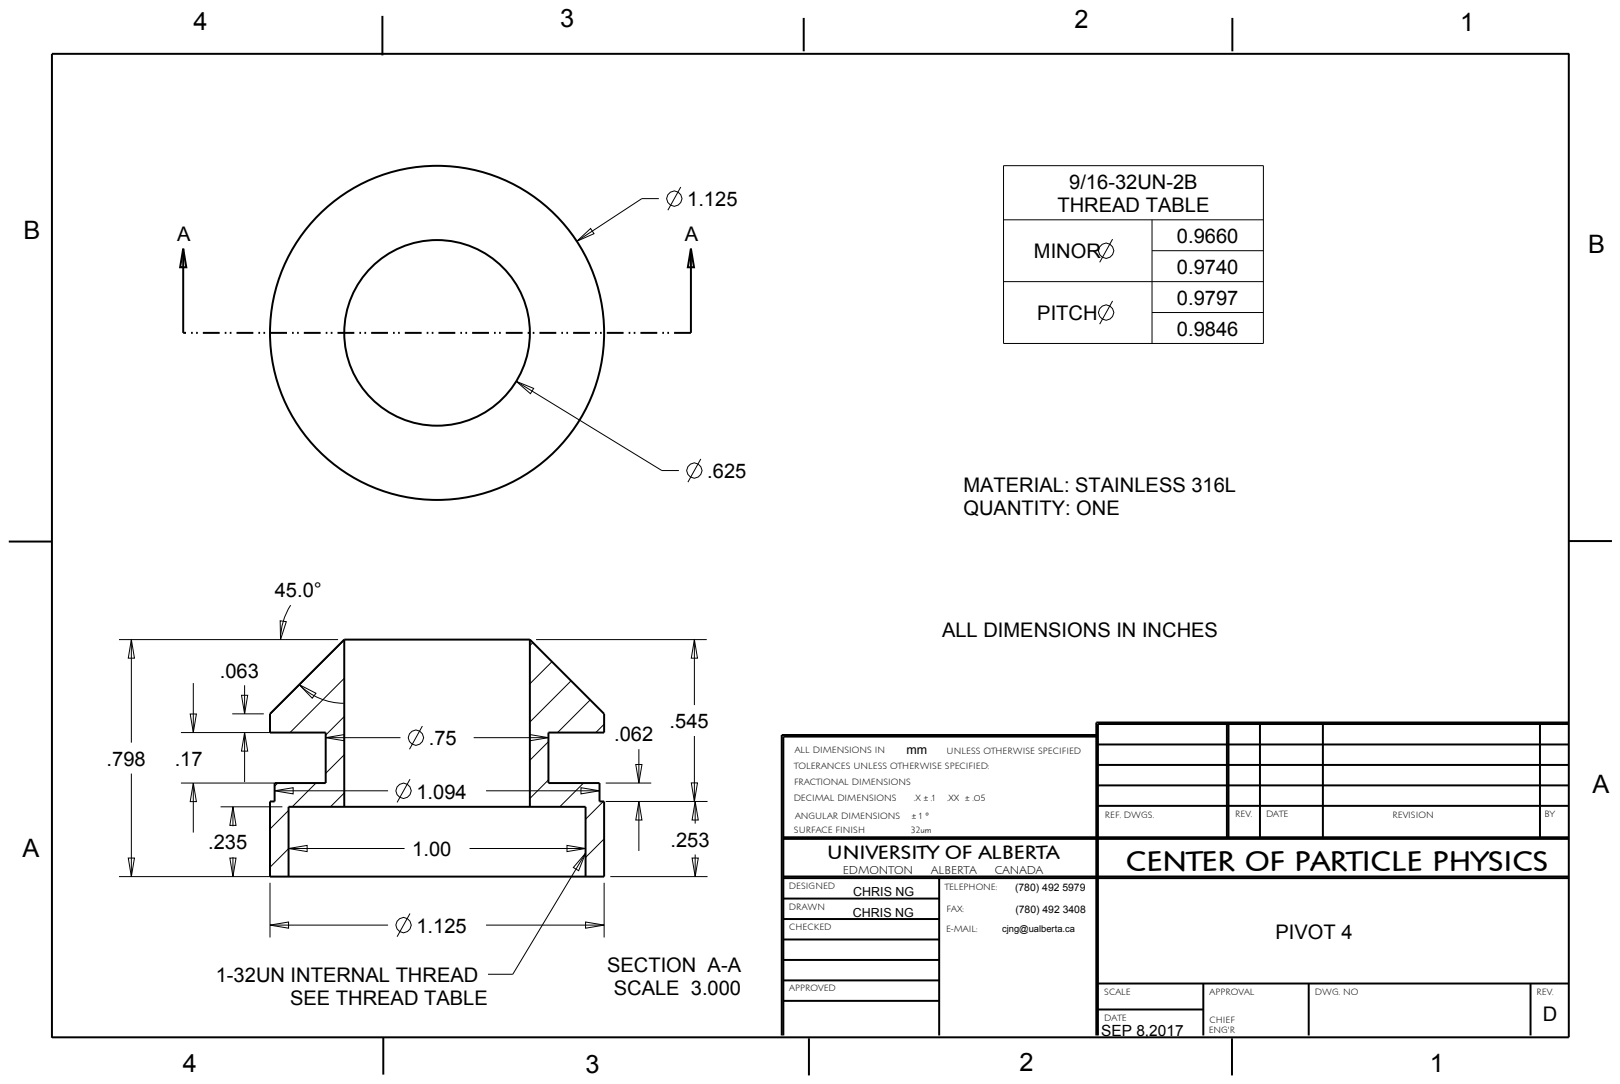
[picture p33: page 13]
DECIMAL DIMENSIONS; SURFACE FINISH; REF. DWGS.; REV.; DATE; REVISION; CHRIS NG; THREAD TABLE; MATERIAL: STAINLESS 316L QUANTITY: ONE; SEP 8,2017; SCALE 3.000

ALL DIMENSIONS IN INCHES

ALL DIMENSIONS IN
TOLERANCES UNLESS OTHERWISE SPECIFIED:
FRACTIONAL DIMENSIONS
ANGULAR DIMENSIONS ± 1 °

mm UNLESS OTHERWISE SPECIFIED

UNIVERSITY OF ALBERTA EDMONTON ALBERTA CANADA | CENTER OF PARTICLE PHYSICS

DESIGNED CHRIS NG | TELEPHONE: (780) 492 5979 FAX: (780) 492 3408 E-MAIL: cjng@ualberta.ca | PIVOT 4

SECTION A-A 1-32UN INTERNAL THREAD
SEE THREAD TABLE

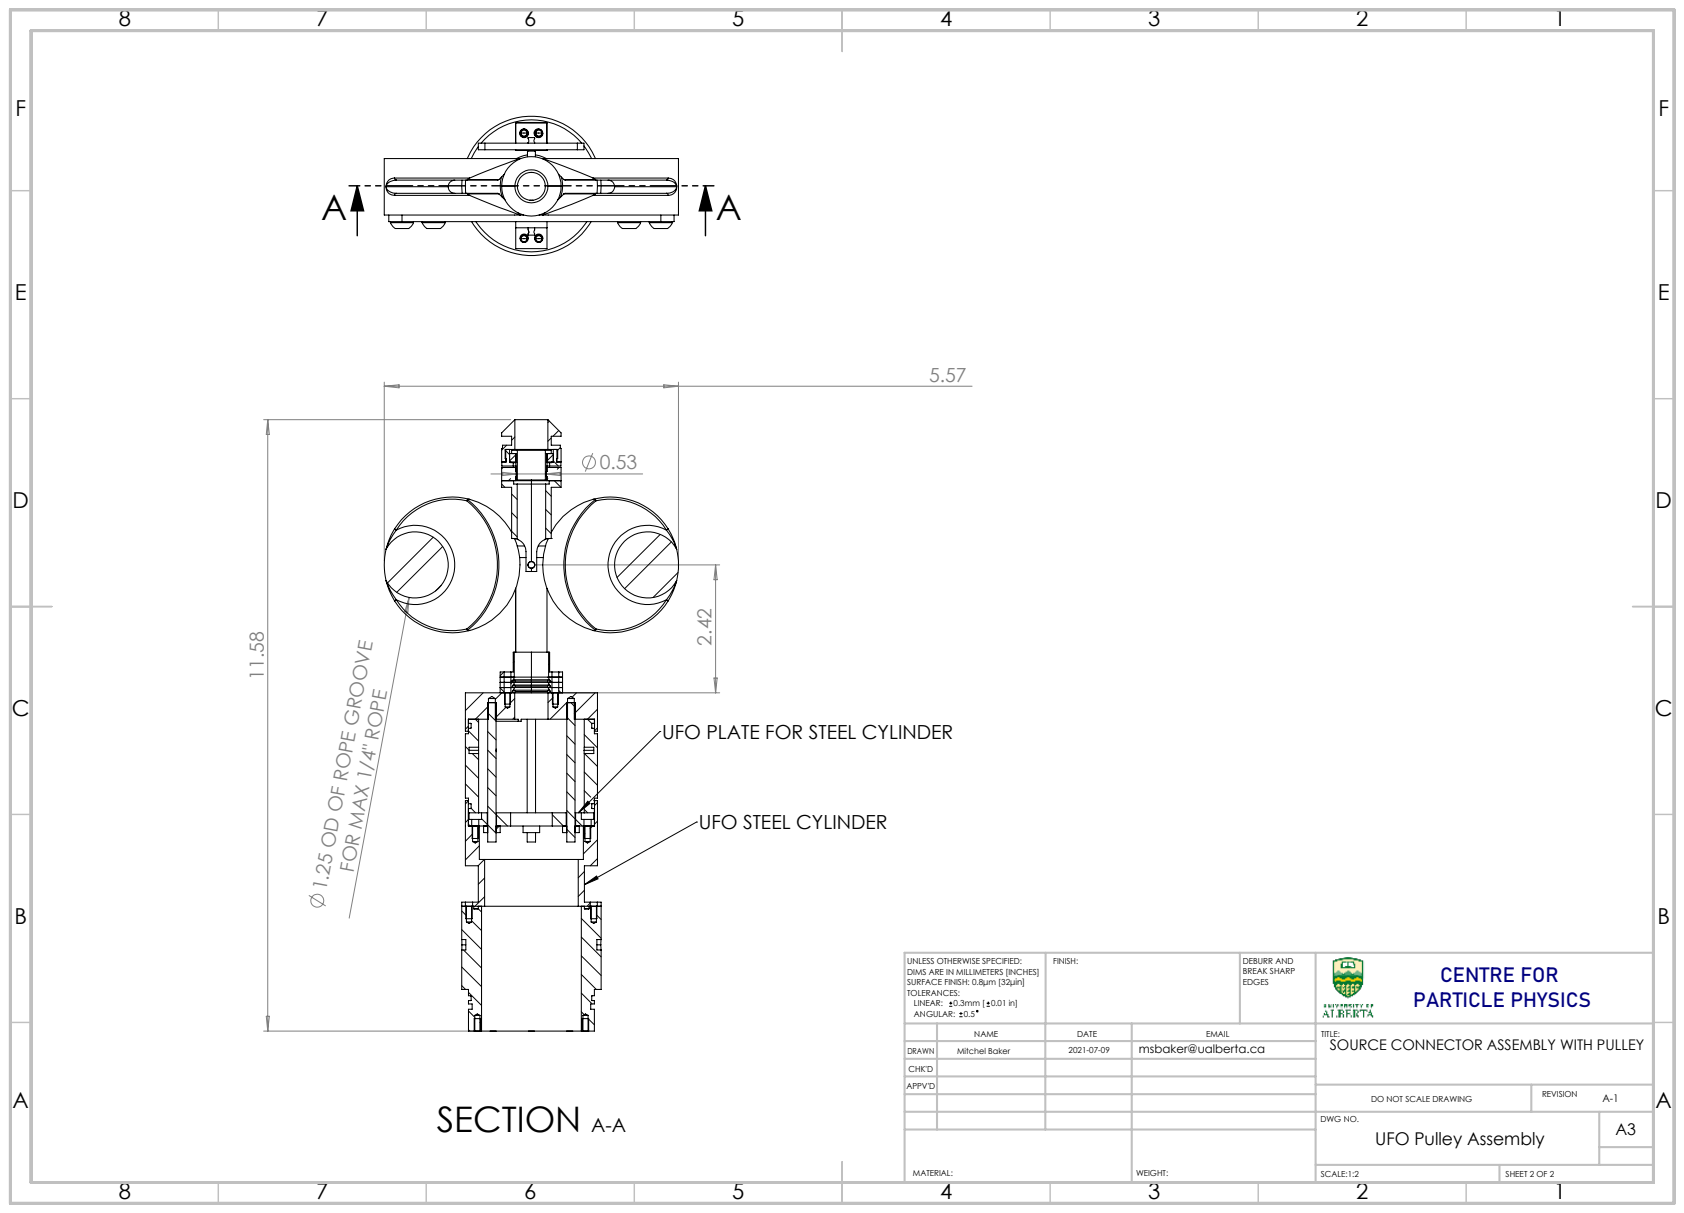
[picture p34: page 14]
SECTION A-A

1.25 OD OF ROPE GROOVE

FOR MAX 1/4" ROPE

UFO PLATE FOR STEEL CYLINDER

UFO STEEL CYLINDER

UNLESS OTHERWISE SPECIFIED: DIMS ARE IN MILLIMETERS [INCHES] SURFACE FINISH: 0.8μm [32μin] TOLERANCES: LINEAR: 0.3mm [ 0.01 in] ANGULAR: 0.5 | FINISH: | DEBURR AND BREAK SHARP EDGES | CENTRE FOR PARTICLE PHYSICS

NAME | DATE | EMAIL | TITLE: SOURCE CONNECTOR ASSEMBLY WITH PULLEY

DRAWN | Mitchel Baker | 2021-07-09 | msbaker@ualberta.ca

CHK'D
APPV'D

DO NOT SCALE DRAWING | REVISION A-1

DWG NO. UFO Pulley Assembly | A3

MATERIAL: | WEIGHT:

SCALE:1:2 | SHEET 2 OF 2

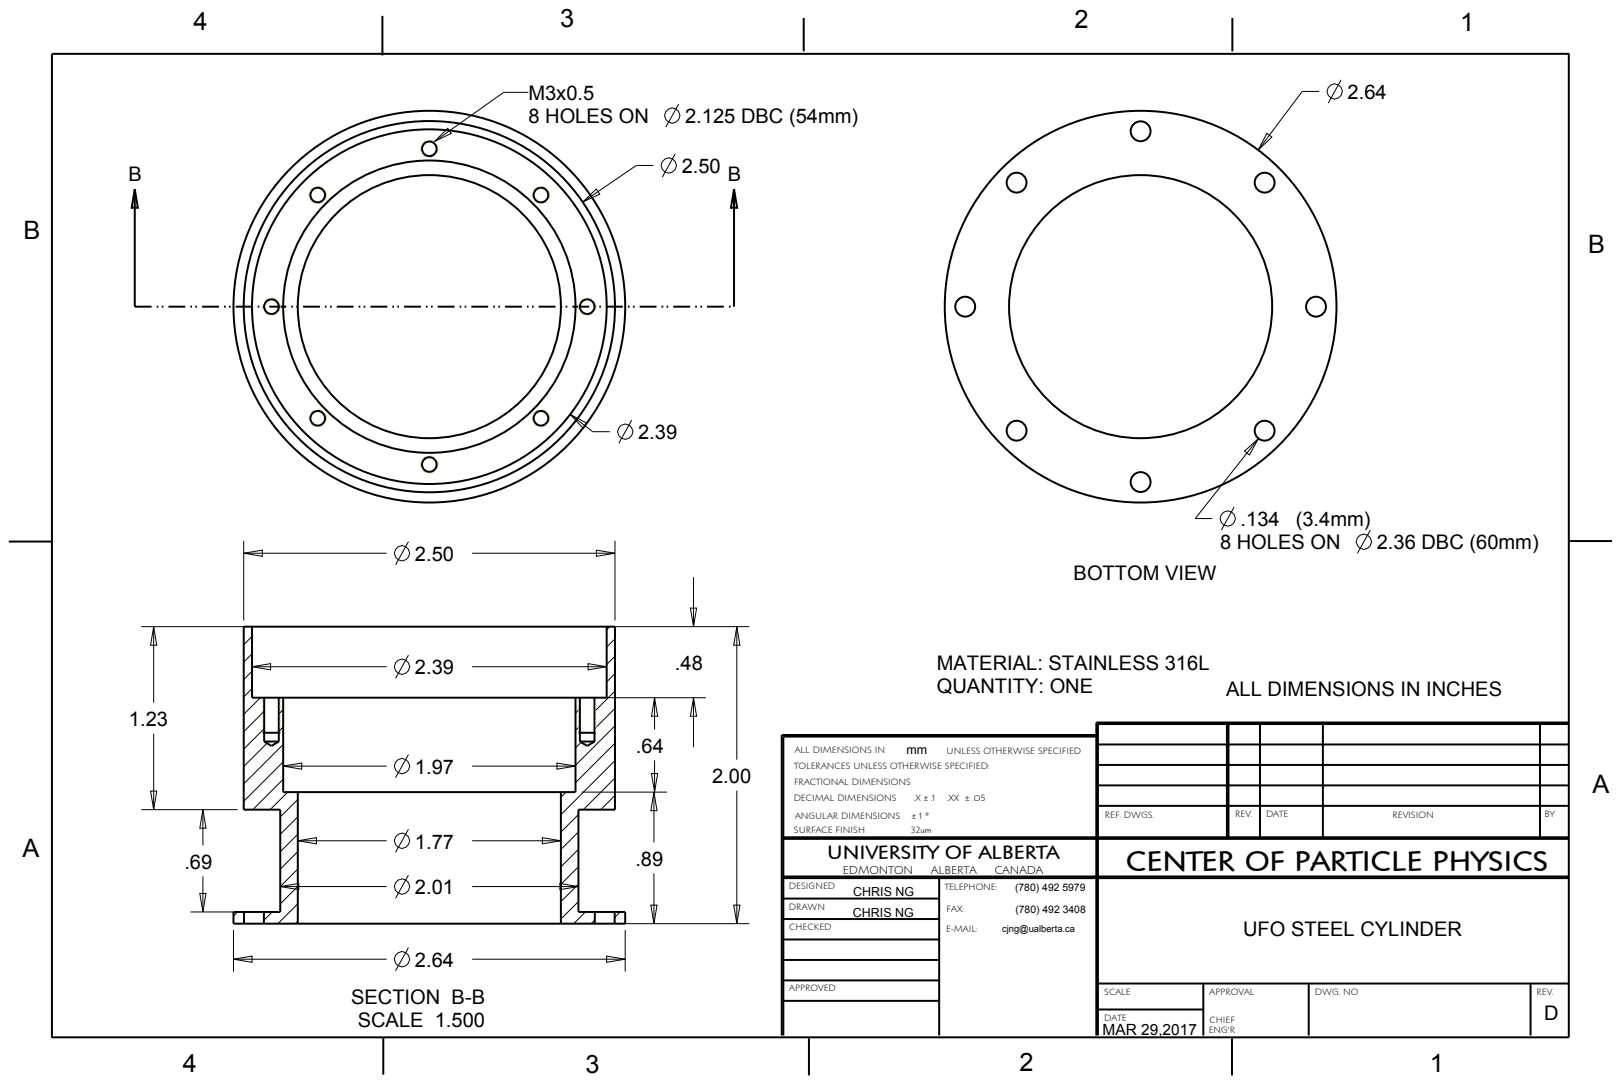
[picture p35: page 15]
DECIMAL DIMENSIONS; SURFACE FINISH; CHRIS NG; 8 HOLES ON; 2.36 DBC (60mm); MATERIAL: STAINLESS 316L QUANTITY: ONE; BOTTOM VIEW; MAR 29,2017 SCALE 1.500; SECTION B-B; 2.125 DBC (54mm)

ALL DIMENSIONS IN INCHES

ALL DIMENSIONS IN
TOLERANCES UNLESS OTHERWISE SPECIFIED:
FRACTIONAL DIMENSIONS
ANGULAR DIMENSIONS ± 1 °

mm UNLESS OTHERWISE SPECIFIED

REF. DWGS. | REV. | DATE | REVISION | BY

UNIVERSITY OF ALBERTA EDMONTON ALBERTA CANADA | CENTER OF PARTICLE PHYSICS

DESIGNED CHRIS NG | TELEPHONE: (780) 492 5979 FAX: (780) 492 3408 E-MAIL: cjng@ualberta.ca | UFO STEEL CYLINDER

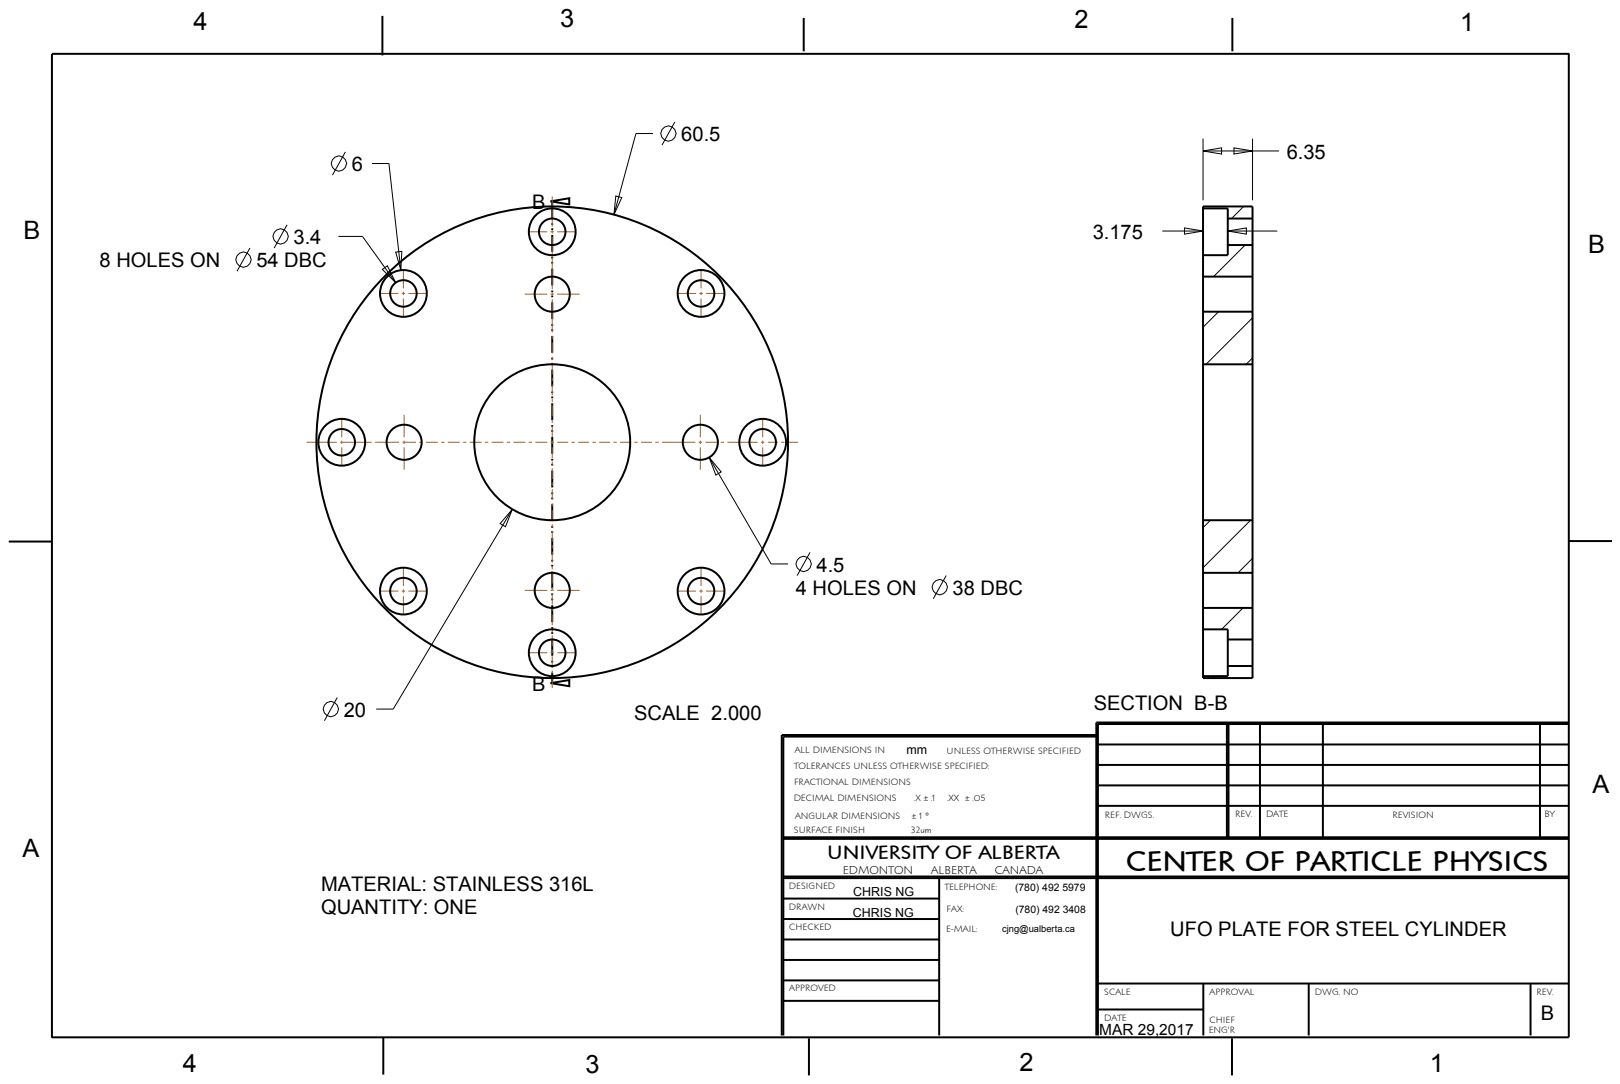
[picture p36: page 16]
DECIMAL DIMENSIONS; SURFACE FINISH; CHRIS NG; 4 HOLES ON; 38 DBC; 8 HOLES ON; 54 DBC; MATERIAL: STAINLESS 316L QUANTITY: ONE; MAR 29,2017; SCALE 2.000; SECTION B-B

ALL DIMENSIONS IN
TOLERANCES UNLESS OTHERWISE SPECIFIED:
FRACTIONAL DIMENSIONS
ANGULAR DIMENSIONS ± 1 °

mm UNLESS OTHERWISE SPECIFIED

REF. DWGS. | REV. | DATE | REVISION | BY

UNIVERSITY OF ALBERTA EDMONTON ALBERTA CANADA | CENTER OF PARTICLE PHYSICS

DESIGNED CHRIS NG | TELEPHONE: (780) 492 5979 FAX: (780) 492 3408 E-MAIL: cjng@ualberta.ca | UFO PLATE FOR STEEL CYLINDER

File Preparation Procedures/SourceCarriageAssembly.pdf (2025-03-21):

# Source Carriage Assembly Instructions

### Ryan Bayes

### November 21, 2024

## 1 Introduction

This document describes the cleaning, handling, and assembly of the elements of the source carriage. This includes the source pivot, the UFO housing, and the source connector (top screw and nut). These parts are not very well documented elsewhere, but they are key to the assembly of the calibration hardware system. These pieces are permanently fixed to the umbilical

## 2 Part Descriptions

### 2.1 Source Pivot

The source pivot is the upper most element of the source assembly. This consists of a nut that fits snugly to the umbilical with a rotating collar (the pivot) intended to provide a tie-off point for the central rope. The pivot attaches to a pully flange, which supports the fixed side rope pulleys, via a pin joint. The assembly supports lower elements of the source via a pair of brackets. Design drawings of the completed assembly are shown in Fig.1.

### 2.2 UFO housing

The umbilical flasher object (UFO) was intended to provide information of the source location to the detector independent of the manipulator system. As the central boards are not ready at this, this functionality will not be available. However the housing for the UFO will be used for the source assembly. The housing consists of a top plate, an acrylic cylinder and a steel

1

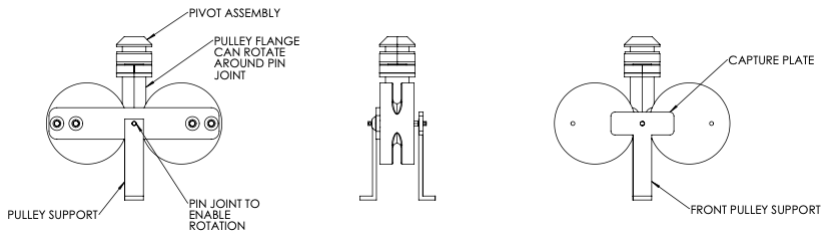
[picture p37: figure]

Figure 1: Source pivot and side rope pulleys

cylinder. The three pieces are held together using long screws that connect the top plate to the steel cylinder through conduits in the acrylic housing. The umbilical is clamped into the UFO housing using a series of pressure plates that are secured to the top plate. The source pivot also attaches to the top plate of the UFO. Design drawings for the UFO cylinder and plate are shown in Fig.2.

### 2.3 Source Connector

The last permainent installation on the umbilical is the source connector. This consists of a barrel with a left handed screw thread on one end which is capped by a feed through which couples the optical fibre in the umbilical to the quartz rod in the Laserball (which terminates in a right hand thread source connector). The source connector and a source (either the Laserball or the AmBe source) are held together with a nut that contains corresponding threads (left handed on the top half, right handed on the bottom half) such that the umbilical side and the source side can be drawn together simply by turning the nut in a clockwise direction while the umbilical and source remain stationary. Alignment rods installed on the source connector plates ensure the source and umbilical alignment through source installation. A detail of the source connector is shown in Fig.3a with a picture of the assembled source connector in Fig.3b.

2

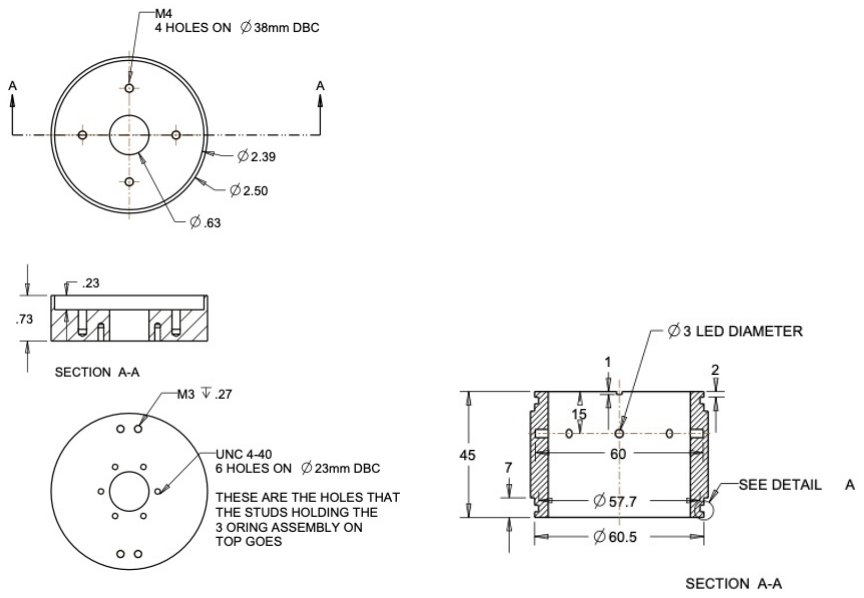
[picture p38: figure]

(a) Top plate | (b) Acrylic cylinder

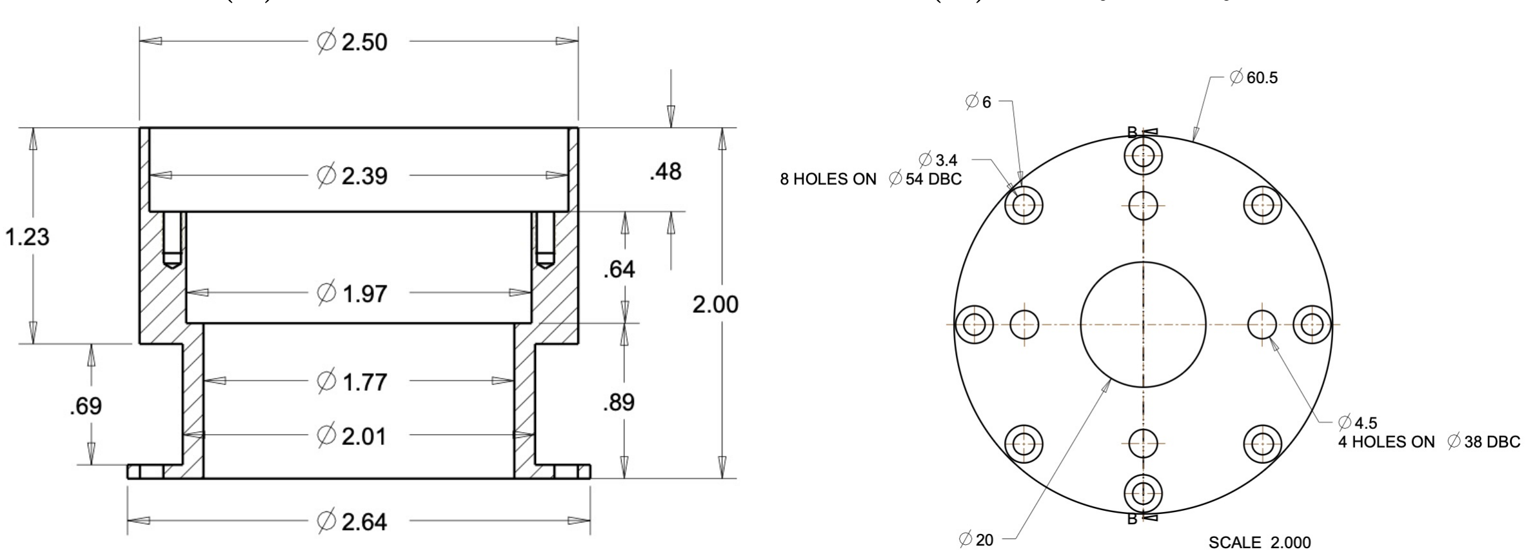
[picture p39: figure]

(c) Steel Cylinder | (d) Acrylic Bottom Plate

Figure 2: Umbilical flasher object housing

3

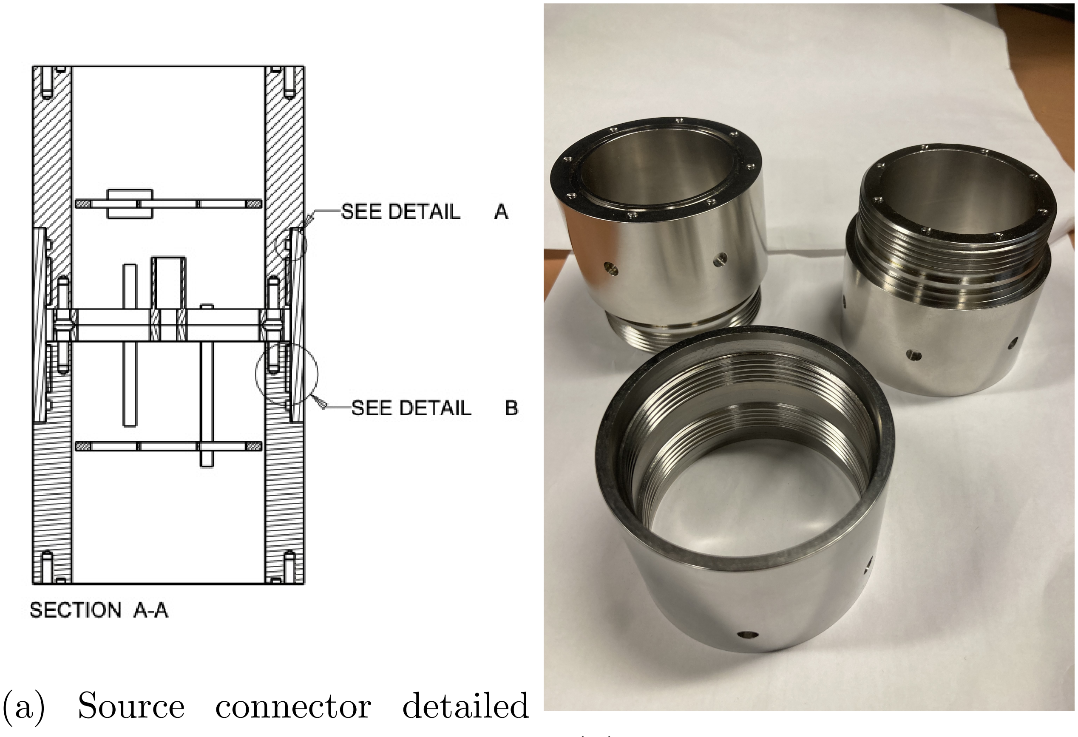
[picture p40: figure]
(a) Source connector detailed

drawing | (b) Source connector in hand

Figure 3: Source connector.

## 3 Cleaning, Handling and Assembly

All of the components of this assembly are stainless steel an acrylic. It is assumed that the majority of cleaning for the various components will be completed using ultra-sonic cleaning. The steps for ultra-sonic cleaning involves

- Placing all of the items in the cleaner basket.
- Fill the US cleaner volume with UPW
- Add NuClean to the volume with a 1:50 concentration (NuClean to UPW)
- Run the cleaner through a 60 minute cycle. This involves heating the volume to 60 degrees celcius, while applying ultra sonic frequencies.
- Drain the cleaner with the components in place. Refill the cleaner volume with UPW. Run the cleaner for 30 minutes for a first rinse.

4

- Drain the cleaner with the components in place. Refill the cleaner volume with UPW and run the cleaner for 60 minutes for a second rinse.
- Drain the cleaner and remove the components from the ultra sonic cleaner
- Dry all of the components with lint free cloths.
- Place the components in plastic bags as appropriate.

Nitrile gloves must be worn at all times when handling the components before, during and after the cleaning procedure.
At the present time, all of the parts for the source pivot assembly are underground, the parts of the source connector and UFO housing are on surface and were cleaned as part of the Laserball preparation, and a second source connector assembly (for the AmBe source) is also on surface and still to be cleaned. The parts that remain on surface are intended to be taken underground by hand after triple bagging all of the components. An additional plastic bag should be added for drift travel, to be removed immediately upon entering the lab. The next most outer bag should be removed before the assembly is moved to the control room. The second to last layer should be wiped down with a lint free cloth and UPW before the assemblage is moved to the DCR.
Assembly of the source carriage assembly requires the cleaned and installed umbilical and central. It may be reasonable to conduct a limited pre-assembly of the source pivot well before the final installation. Assembly consists of
□ | 1. Wet the bottom metre of umbilical with LAB
□ | 2. Pre-wet all of the screws with LAB
□ | 3. Install o-rings on the UFO acrylic cylinder, the source connector top and bottom surfaces.
□ | 4. Threading the umbilical through the pivot
□ | 5. Thread the umbilical through the pressure plates with appropriate o- rings.

5

□ | 6. Thread the umbilical through the top plate of the UFO.
□ | 7. Ensuring that there is a surplus of umbilical below the top plate of the UFO run the umbilical through the UFO acrylic, steel plate and stainless steel cylinder, and the upper source connector body.
□ | 8. Couple the end of the fibre bundle to the source connector plate.
□ | 9. Secure the source connector plate to the source upper source connector body with 8 m2 screws.

□ 10. Fasten the UFO bottom plate to the top of the UFO steel cylinder.

□ 11. Align the acrylic cylinder between the top section and the UFO plate
| and thread the support rods into the top plate. Once the threaded rod is secured, tighten the UFO assembly together using the appropriate nuts.

□ 12. Fasten the UFO steel cylinder to the top of the upper source connector
| with 8 m3 cap screws.

□ 13. Tighten the presure plates against the top of the UFO assembly using
| four M3 screws.

□ 14. Secure the source pivot pully support plates to the UFO assembly.

□ 15. Tie the central rope to the rotating collar on the pivot assembly.

| Questions: • Do we have the pressure plates with the Laserball? Are these plates elsewhere? • Does the source pivot clamp down on the umbilical?
| • Is there enough room to turn a wrench to secure the threaded rod?
| • Is the fibre bundle assembly procedure written elsewhere?

6

## 4 Usage

Once the source connector has been assembled with the umbilical, sources can be exchanged with little difficult. At this time only two sources are planned; the Laserball and the AmBe source. Installation of the laserball is the more sensitive of the two. The steps for this involve two people equipped with standard PPE and nitrile gloves. Assuming the source connector is exposed below the bellows gate valve;

□ | 1. Remove the source connector end of the source from it’s storage bag (leave the diffuser inside the bag).
□ | 2. Match the source connector to the umbilical source connector with the nut between them using the guide studs to locate the relative location of the two plates.
□ | 3. With the help of a collegue push the two source connector ends together until they meet the threads of the nut, then hold the source connector ends in place while turning the nut clockwise. • If the nut does not thread easily, the nut will have to be flipped. • If there is any resistance before the nut is completely threaded stop, check the orientation of guide studs and the alignment of the quartz rod before starting over.
□ | 4. With the nut completely threaded, the complete source assembly should be snugly in place. Test by applying a little more force in the clockwise direction.
□ | 5. Remove the bag from the diffuser flask. Raise the source into the URM.
| These steps will be identical for the AmBe source except there will be be no guid rods to align as there is no optical rod to match.

7

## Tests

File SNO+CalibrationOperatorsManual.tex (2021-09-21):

\documentclass[10pt]{report}
\usepackage{geometry}                % See geometry.pdf to learn the layout options. There are lots.
\geometry{letterpaper}                   % ... or a4paper or a5paper or ... 
%\geometry{landscape}                % Activate for for rotated page geometry
%\usepackage[parfill]{parskip}    % Activate to begin paragraphs with an empty line rather than an indent
\usepackage{graphicx}
\usepackage{amssymb}
\usepackage{epstopdf}
\DeclareGraphicsRule{.tif}{png}{.png}{`convert #1 `dirname #1`/`basename #1 .tif`.png}

\usepackage[english]{babel}
\usepackage[utf8]{inputenc}

\usepackage{fancyhdr,ragged2e}
\fancyhead{}
\lhead{\parbox[t]{0.4\textwidth}{\RaggedRight\rightmark\strut}}
\rhead{\parbox[t]{0.4\textwidth}{\RaggedLeft\leftmark\strut}}
\setlength{\headheight}{5\baselineskip}
\pagestyle{fancy}

\usepackage{verbatim}
\usepackage{hyperref}
\usepackage{geometry}
\usepackage{siunitx}
% \geometry{top=2in}

\title{SNO+ Calibration Operator's Manual}
\author{Ryan Bayes, Rachel Richarson, Cindy Lin, Matt Depatie, \\ adapted from SNO Calibration operator's Manual by Peter Skensved and Fraser Duncan}
\date{\today}

\begin{document}
\maketitle
% try to refactor sections based on readme
\pagebreak
\part{Overview}
\include{Overview/Introduction}
\chapter{Manipulator}
\include{Overview/Manipulator}
\chapter{Calibration Systems Overview}
\include{Overview/Geometry}
\include{Overview/CalibrationGasSystem}
\include{Overview/Laser}
\include{Overview/Laserball}
\include{Overview/Cherenkov}
\include{Overview/N16}
\include{Overview/AmBe}
\include{Overview/TaggedSource}
\chapter{Manipulator Procedures}
\include{Manipulator/body}
\chapter{Laser Procedures}
\include{Laser/body}
\chapter{DT Generator Procedures}
\include{DTGenerator/body}
\include{SaltOven/body}
\chapter{Pumping and Perging Volumes}
\part{Water Calibration Procedures}
\chapter{Laserball PCA}
\include{StandardCalibrations/LaserballPCA_body}
\chapter{N16 Calibration}
\include{StandardCalibrations/N16Calibration_body}
\chapter{Encapsulated Sources Calibration}
\include{StandardCalibrations/Encapsulated_body}
\chapter{Cherenkov Source Calibration}
\include{StandardCalibrations/CherenkovDeployment_body}
\part{Scintillator Calibration Procedures}
\chapter{Source Handling Procedures}
%\include{ScintillatorSourceHandling/SourceHandlingBody}
\include{ScintillatorSourceHandling/SCV_Referencemanual}
\include{ScintillatorSourceHandling/SCV_Operator_Manual}
% should also include specific cleaning procedures in this section
\chapter{URM Procedures}
% Maybe include umbilical cleaning procedures here
\include{ScintillatorURMHandling/ScintURMLifting}
\include{ScintillatorURMHandling/ScintURMMounting}
\include{ScintillatorURMHandling/PumpPurge}
\chapter{Source Deployment Procedures}
\include{ScintillatorDeployment/LaserballPCA}
\include{ScintillatorDeployment/AmBeCalibration}
\include{ScintillatorDeployment/TaggedSourceDeployment}
\include{ScintillatorDeployment/CherenkovDeployment}
\end{document}

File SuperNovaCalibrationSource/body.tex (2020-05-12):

\section{Purpose}
To define the safe operating procedures for the Class 3B laser used for supernova calibration of the SNO+ detector. The supernova calibration source will be used as a way to predict the response of the SNO+ detector to a supernova event, acting as a "stress-test" for the detector.

\section{Description}
The laser diode in use for the SNO+ Supernova Calibration Source is a 405nm laser diode that has a peak power of approximately 240mW [1]. The laser diode is optically coupled by an optical fiber to the SNO+ laser ball that can be deployed into SNO+, externally or internally, using an Umbilical Retrival Mechanism (URM). The procedures outlined in this document should be used in conjunction with the "SNO+ Laser Ball PCA Procedures" for the deployment of the laser ball. Additional information on the supernova source components and characteristics can be found in Caitlyn Darrach's thesis[1].  
\begin{figure}[h] 
\vspace{0.5cm}
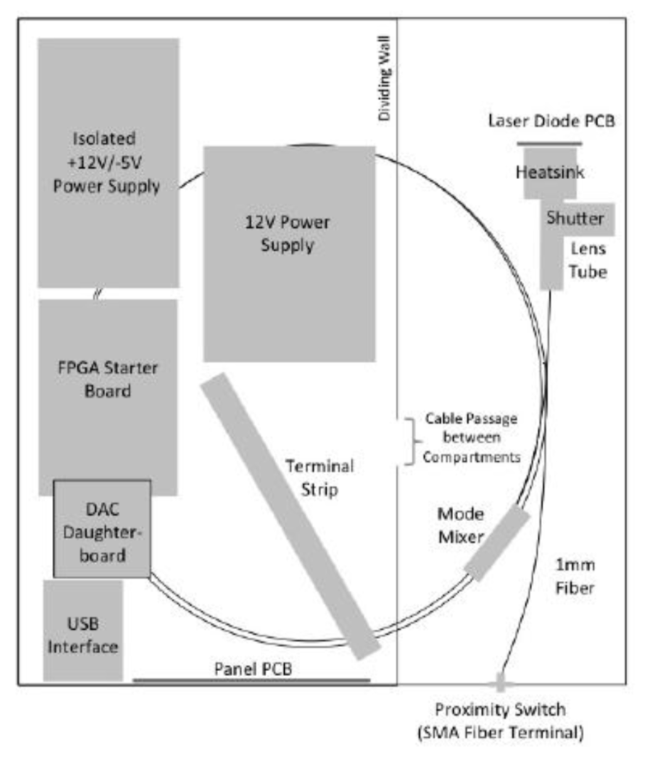
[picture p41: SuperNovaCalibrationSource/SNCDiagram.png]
{\centering{\par}}
\captionsetup{justification=centering}
\caption{Diagram of the components in the Supernova Source box [1]. Note that the proximity switch will automatically close the shutter if nothing is connected to it as a safety precaution.} 
\end{figure}
\section{Training}
All personnel working in the vicinity of the laser when in operation will have completed SNOLAB's \href{https://www.snolab.ca/docushare/dsweb/Get/ControlledDocument-264/SL-MCS-EHS-60-020-P-Lasers-and-UV-Irradiation-Devices-Safety-Program_Rev_01.pdf}{laser safety training} and have completed the "Laser Worker Confirmation of Training" form. An ophthalmic examination may be required. \\
Personnel should also be trained in the operation of the SNO+ calibration equipment related to the deployment of the laser ball and follow associated procedures. 

\section{Potential Hazards and Risks}
The laser in the supernova source is considered a Class 3B laser as it is a 240mW (peak power) laser. 

\underline{Eye}
\begin{itemize}
\item A Class 3B laser poses a moderate risk of eye injury if precautions aren't taken. 
\item Eye injury is possible if the retina is exposed to the beam or reflection of the beam. 
\end{itemize}

\underline{Skin}
\begin{itemize}
\item A Class 3B laser is not normally considered a skin or materials burn hazard. However, if the laser is kept motionless on skin at close range, heat can be felt. 
\end{itemize}

\section{Precautions}
\begin{itemize}
    \item Laser operators must read and understand the safe operating procedures for the laser prior to use and be trained to use lasers at SNOLAB
    \item The laser must be inspected prior to each use
    \item Ensure that there is enough time to complete all work so as to avoid rushing
    \item Avoid all exposure to the laser light
    \item Ensure that appropriate laser warning signs are displayed before the laser is operated and that all personnel in the area are aware that the laser will be in use
    \item When possible, have ambient light in the area of laser use. This keeps the pupil constricted, reducing the possibility of eye damage
    \item Keep all protective covers on the laser when in use
    \item Avoid wearing jewellery or other reflective objects during laser operation. Ensure that the area around the laser is also free from reflective surfaces
    \item Don't use the laser with a greater intensity than needed
\end{itemize}
\section{Personal Protective Equipment}
\begin{itemize}
\item Protective eye ware suitable for the wavelength of the laser must be worn at all times during the operation of the laser. 
\item Any jewellery or otherwise reflective objects should be removed 
\end{itemize}
\section{Operating Procedure}
The key for the interlock for the laser should be kept in the SNO+ Deck Clean Room (DCR) desk when not in use. \\ \\
\textbf{Pre-Operation Procedures}
\begin{enumerate}
\begin{checklist}
    \item Post laser warning signs on the door to the Deck Clean Room (DCR) including a contact name 
    \item Advise anyone already working in the area that the laser will be in use and provide appropriate laser protective goggles
    \item Check that the optical fiber is correctly connected to the source (SMA Fiber Output, see Figure 1) and that the other end is properly connected to the laser ball. The supernova calibration source has a fail-safe so that if the optical fiber is disconnected at the source box the shutter will be automatically closed. 
    \item Locate the laser interlock key and ensure that the shutter enable is in the "CLOSED" position 
\end{checklist}
\end{enumerate}
\textbf{Operation Procedures}\\
Please note that this procedure covers the operation of the Supernova Calibration laser only. This procedure should be used in conjunction with the "SNO+ Laser Ball PCA Procedures", ignoring parts that reference the N2 laser.\\ \\
\begin{figure}[h] 
\vspace{0.5cm}
{\centering{\par}}
\captionsetup{justification=centering}
\caption{View of the LabView user interface used to run the Supernova source and monitor its status [1].} 
\end{figure}
\begin{figure}[h] 
\vspace{0.5cm}
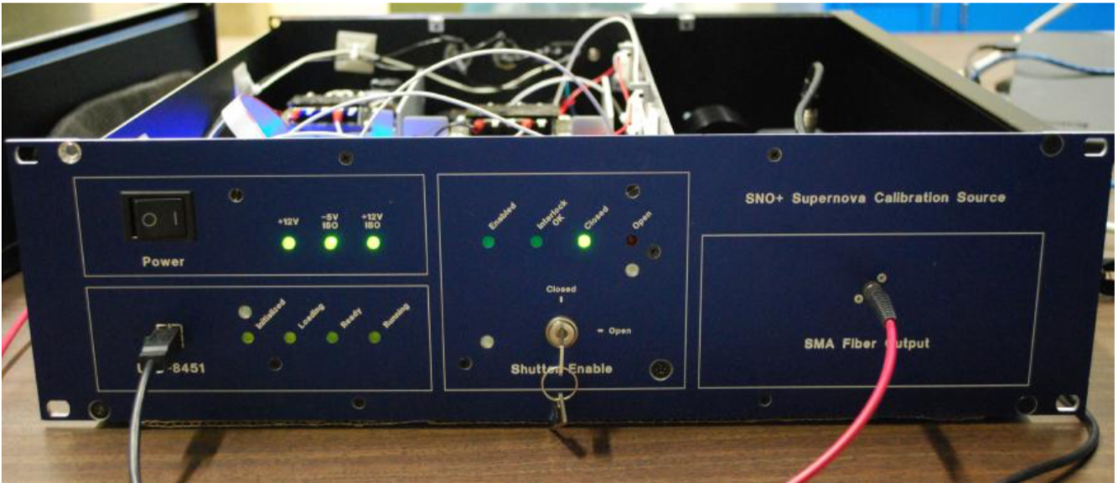
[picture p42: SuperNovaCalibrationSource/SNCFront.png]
{\centering{\par}}
\captionsetup{justification=centering}
\caption{View of the front panel of the SNO+ Supernova Calibration Source [1]. Not that the top panel is removed for this picture but would be in place during operation.} 
\end{figure}
\underline{Start-Up}
\begin{enumerate}
\begin{checklist}
    \item Log-on to the computer connected to the source (Password: s******va)
    \item Open the LabWindow program and load SNCplus
    \item Power on the supernova source
    \item Load the look up tables
    \item Set the idle DAC Value to 23,000 (activation current for the laser)
    \item Load the pulser and FIFO buffer
    \item Turn the interlock key on the source box to the "OPEN" position for the shutter
    \item Start the run by pressing "RUN" on the computer. The front panel of the laser source should display that it is "RUNNING" and that the shutter is "OPEN" (See Figure 1)
\end{checklist}
\end{enumerate}
\underline{Shut-Down}
\begin{enumerate}[resume]
\begin{checklist}
    \item Ensure that the supernova run has ended
    \item Turn the shutter interlock key to the "CLOSED" position.
    \item Power off the supernova source
    \item Save any required information
    \item Log out from the computer
\end{checklist}
\end{enumerate}
\textbf{Post-Operation Procedures}
\begin{enumerate}
\begin{checklist}
    \item Remove the key from the supernova source and return it to its designated location
    \item Remove laser warning signs and advise anyone in the area that the laser is no longer in use
\end{checklist}
\end{enumerate}
\section{Emergency Procedure}
In the event that the laser needs to be turned off quickly there is an emergency stop button located in the SNO+ control room that will stop the operation of the laser. 

\section*{Reference}
[1] Darrach, Caitlyn. {\itshape The SNO+ Supernova Calibration Source Development and Testing}. 2016.
\newline

\appendix

\section{Revision History}
\begin{center}
\begin{tabular}{|c|c|c|c|}
\hline
     \textbf{Revision} & \textbf{Date} & \textbf{Author} & \textbf{Details}  \\
     \hline
     1& & & First Draft \\
     \hline
\end{tabular}
\end{center}

\end{document}

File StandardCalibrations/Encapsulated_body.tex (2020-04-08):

\fancyhf{}
% \lhead{\begin{tabular}{|p{8.25cm}} \hline {\large \bf SNO+ Laser Procedures} \\ \\ \\ \\ \end{tabular}}
\lhead{\begin{tabular}{|p{8.25cm}|p{6cm}|}  
	\hline 
		{\large \bf Acrylic Calibration Procedure}  
										& Document No:  \\ 
								\cline{2-2} & Revision No: 01\\  
								\cline{2-2} & Effective Date: 2017-08-25\\ 
								\cline{2-2} & Page \thepage \\  \end{tabular}}

\begin{tabular}{||l|l|l||}
\hline\hline
& \multicolumn{2}{p{8cm}||}{\bf Encapsulated Calibration Procedure} \\
 & \multicolumn{2}{p{8cm}||}{} \\
\hline
\multicolumn{2}{||p{8.5cm}|}{Document Number:} & Revision Number: 01\\
\hline
\multicolumn{3}{||l||}{Document Owner: SNO+ Calibration Post-Doc} \\
\hline
\multicolumn{3}{||l||}{Reviewer:}\\
\hline
Name: & Signature & Date \\
\hline
\multicolumn{3}{||l||}{Authorizer:}\\
\hline
Name: & Signature & Date \\
\hline\hline
\end{tabular}
\thispagestyle{empty}

\section{Purpose}

The procedure describes step by strp the deployment process for an
acryilic source into the AV. It is basically identical to the
Laserball or N16 deploment procedure. It is intendedd as a guideline
for operators who have been trained on the manipulator and laser. It
assumes that the laserball is mounted on URM2 which is located on the
10'' gatevalve on the UI.

The outline of the procedure is:
\begin{enumerate}
\item Prepare the URM for use (turn on N$_{2}$ supply etc).
\item Flush URM2 with N$_{2}$ gas to remove O$_{2}$ and Rn.
\item Calibrate URM2 central rope.
\item Lower source into glovebox.
\item Conneect side ropes to source (if not single axis mode).
\item Deploy source into detector.
\item Take data.
\item Retract source into UI.
\item Remove side ropes (if not single axis mode).
\item Retract source inot source tube above gatevalve.
\item Shut down gas flow to URM.
\end{enumerate}

% \begin{form}

\begin{tabular}{|l|l|}
\hline
\multicolumn{2}{|l|}{} \\
\multicolumn{2}{|l|}{\bf Encapsulated Calibration Procedure} \\
\multicolumn{2}{|l|}{} \\
\hline
& \\
\TextField[name=acalop,backgroundcolor=0.975 0.975 0.975,width=2cm]{Operator: } &
\TextField[name=acald,backgroundcolor=0.975 0.975 0.975,width=4cm]{Date: } \\
& \\
\hline
\end{tabular}

The procedures in this section are intended to be followed
sequentially fro the source calibration except where it is noted the a
following procedure can be skipped. Specifically if the source run is
to be done in {\it single axis} mode, the side ropes do not need to be
attached or detached from the source.

{\bf Prior to Calibration Run}
\begin{enumerate}
  
\item \CheckBox[name=encp1]{} Permission for procedure and confirmation of equipment rediness
  has been received from Head of Calibration Group.
  
  \begin{center}
    \begin{tabular}{|l|}
      \hline
      \\
      \TextField[name=acalHCG,backgroundcolor=0.975 0.975
        0.975,width=2cm]{Authorizor's name:}
      \\
      \hline
    \end{tabular}
  \end{center}
  
\item \CheckBox[name=encp2]{} Source is mounted in URM2 which is mounted on 10'' valve on UI.
\item \CheckBox[name=encp3]{} 10'' gatevalve is closed and locked.

  {\bf Readying URM from Operation}

  \item \CheckBox[name=encp4]{} Verify that the LN$_{2}$ dewar in the junction is at least 1/4
    full. If not sway is out with another dewar. Record the liquid
    level of the dewar.
    
    \begin{center}
      \begin{tabular}{|l|}
        \hline
        \\
        \TextField[name=ln2level,backgroundcolor=0.975 0.975
          0.975,width=2cm]{LN$_{2}$ Level:}\\
        \\
        \hline
      \end{tabular}
    \end{center}
    
\item \CheckBox[name=encp5]{} Verify that the dewar gas pressure is approximately 130 to 150
  psig. If not, swap it out with another dewar.
\item \CheckBox[name=encp6]{} Turn on N$_{2}$ flow to laser from dewar at junction.
  
  \begin{center}
    \begin{tabular}{|l|}
      \hline
      \\
      \TextField[name=n2time,backgroundcolor=0.975 0.975 0.975,
        width=2cm]{Note Time:}\\
      \\
    \end{tabular}
  \end{center}

\item \CheckBox[name=encp7]{} Turn on pressure builder valve. {\it the pressure builder opens
  a controlled leak on the dewar to maintain the 150 psi pressure
  head. If the valve is not opened, the gas pressure to the laser
  will eventually drop below the operating level.}
\item \CheckBox[name=encp8]{} Once the URM is flushed, the N$_{2}$ supply may be switched
  from the high pressure dewar to the Wessington dewar. Check with
  the Operations Group first before switching. Do not use the
  Wessington if a transfer is in progress. Consult the gasboard
  section for details on how to switch.
\item \CheckBox[name=encp9]{} Contact Detector Operator and get permission to enter DCR. Make
  sure that the DCR activity bit is set.
\item \CheckBox[name=encp10]{} Turn on lights in DCR following standard procedure. (See
  Detector Operator Manual)
\item \CheckBox[name=encp1]{} Remove the flush return line on the URM. {\it The presence of the
  buffer line makes it difficult to measure the O$_{2}$ from the URM.}
\item \CheckBox[name=encp11]{} Check that the flush inlet line is connected to URM2. If not
  connect it. Open the valve on the source tube. {\it It may be
    necessary to valve off other URMs to get sufficient flow.}
\item \CheckBox[name=encp12]{} Set up Gas Board in `bypass mode' for `URM flush' only. If you
  are using the high pressure feed {\bf do not exceed} 10 psi on the
  regulator. {\it Bypass mode maximizes the flow to the URM.}
\item \CheckBox[name=encp13]{} Check that the flow meter (located at the South-East corner of
  the pipe box) is railed. If not, open needle valve near the
  flowmeter fully. {\bf Flush should continue until O$_2$ reading at
    the rear of the URM is less than 0.8\%.} {\it This may take up to
    an hour depending on when the URM was last flushed.}
\item \CheckBox[name=encp14]{} Check that the source clamps are in the OUT position. {\bf Both}
  knobs have to be in the extreme {\bf OUT} position. {\bf WARNING: If
    the source is moved with the clamps in the IN position, the
    source, umbilical and manipulator may be severely damaged!} {\it
    The clamps are used to secure the source while the URM is being
    moved on and off the glovebox.}
\item \CheckBox[name=encp15]{} Check the pressure on the air cylinder for the umbilical takeup
  mechanism. It should be between 45 and 55 psig. {\bf DO not operate
    the URM if the pressue is below 40 psig}. If the pressure falls
  below 10 psig at any point (even momentarily) call the OCE. An
  internal inspection of the URM is mandatory before operating the
  unig again. {\it The pressure cylinder on the URM maintains tension
    on the umbilical takeup reel. A low gas pressure can result in the
    umbilical falling off the takeup reel and getting caught or jammed
    leading to destruction of the umbilical.}
\item \CheckBox[name=encp16]{} Verify that the 10'' gatevalve is locked in the closed
  position. {\it The valve is CLOSED when the hangle points in toward
    the pipes and the slot on the handle stem points AWAY from the
    source tube.}
\item \CheckBox[name=encp17]{} Calibrate Central Rope Length (see procedure). Record changes in
  length of central rope and umbilical. The current fiducial mark for
  URM2 on the 10'' gatevalve is
  \[
  z_{mark} = 1549.3
  \]
  Note: the fiducial mark is written on the source tube. If it
  differes from the above number use it instead.

  \begin{center}
    \begin{tabular}{l}
      \hline
      \\
      \TextField[name=crcal1,backgroundcolor=0.975 0.975 0.975,
        width=2cm]{$\Delta$l rope:} \\
      \\
      \hline
      \\
      \TextField[name=cucal1,backgroundcolor=0.975 0.975 0.975,
        width=2cm]{$\Delta$l rope:} \\
      \\
      \hline
    \end{tabular}
  \end{center}

\item \CheckBox[name=encp18]{} Check that all seals are in place on URM. Including:
  \begin{itemize}
  \item \CheckBox[name=encp19]{} flush inlet line
  \item \CheckBox[name=encp20]{} window on front of URM motorbox
  \item \CheckBox[name=encp21]{} window on rear of URM motorbox
  \item \CheckBox[name=encp22]{} umbilical feedthrough on rear of motorbox
  \item \CheckBox[name=encp23]{} view port window cover on source tube
  \item \CheckBox[name=encp24]{} window on rear of stretcher box
  \end{itemize}
\item \CheckBox[name=encp25]{} Wait until the O$_{2}$ level in the URM is at or below 0.8\%

  \begin{center}
    {\bf Deploying Source rfom Source Tube Into Glovebox}
  \end{center}
  
\item \CheckBox[name=encp26]{} Verify that the URM is below 0.8\% O$_{2}$.
\item \CheckBox[name=encp27]{} Check that flush return line is connected to URM2. If not
  connect it. {\it It may be necessary to move it from another URM.}
\item \CheckBox[name=encp28]{} Turn off DCR lights.
\item \CheckBox[name=encp29]{} Record the Cover Gas O$_{2}$ level
  \begin{center}
    \begin{tabular}{l}
      \hline
      \\
      \TextField[name=cg0ra,backgroundcolor=0.975 0.975 0.975,
        width=2cm]{Cover Gas O$_{2}$ Reading:}\\
      \\
      \hline
    \end{tabular}
  \end{center}
\item \CheckBox[name=encp30]{} Establish communication with the detector operator. Ensure that
  the detector is in a Transition run. The detector operator should
  monitor the detector rates.
\item \CheckBox[name=encp31]{} Open gate valve ({\bf Slowly!}.\\
  Record the time the valve is opened.
  \begin{center}
    \begin{tabular}{|l|}
      \hline \\ \TextField[name=tgvoa,backgroundcolor=0.975 0.975 0.975,
        width=2cm]{Time Gate Valve Opened}\\
      \\
      \hline
    \end{tabular}
  \end{center}

\item \CheckBox[name=encp32]{} Secure the gate valve either by locking or removing the handle.
\item \CheckBox[name=encp33]{} With flashlight, and participation of the detector operator,
  perform a light leak check on the URM. In particular, check the seal
  of the source tube window and around the base of the source
  tube. Also, check around any inspection panel which may have been
  removed in the recent past.
\item \CheckBox[name=encp34]{} Bring up the lights on breaker 9 in the DCR with the detector
  operator monitoring the detector rate.
\item \CheckBox[name=encp35]{} Verify that {\bf manip\_logger} is running on the calibration
  computer and is logging the Encapsulated source by checking the latest
  entries in couch.ug.snopl.us/manip/\_all\_docs.
\item \CheckBox[name=encp36]{} Check movement of the acrylic source down:
  \begin{center}
    \begin{tabular}{|l|l|}
      \hline
      console & \verb+manip > ambe by 0 0 -5+ \\
      \hline
      manmon & in ambe window: \\
      & set x=0, y=0, z=-5\\
      & click on {\bf move by} \\
      \hline
    \end{tabular}
  \end{center}
  {\it The source should move down 5 cm. The tension on the rope
    should be 40-60 N. The tension on the umbilical should be 10-30
    N.}
\item \CheckBox[name=encp37]{} Check that the source offset is set correctly. At the console
  type \verb+acrylic sourceoffset+. The actual offset depends on the
  exact configuration (canned/un-canned, spacer present etc.)
\item \CheckBox[name=encp38]{} Deploy source into the glovebox:
  \begin{center}
    \begin{tabular}{|l|l|}
      \hline
      console & \verb+manip > ambe to 0 0 1380+ \\
      \hline
      manmon & in ambe window: \\
      & set x=0, y=0, z=1380\\
      & click on {\bf move to} \\
      \hline
    \end{tabular}
  \end{center}
\item \CheckBox[name=encp39]{} Contact Water Supervisor and advise him/her that the source is
  being lowered into the D$_{2}$O. {\it The water group maintains a
    very small differential pressure between the water inside and
    outside of the heavy water. The volume of the source is enough to
    disrupt this differential pressure.}
\item \CheckBox[name=encp40]{} Check tension of urm2rope and urm2umbilical. Rope tension should
  be approximately 30-50 N. Umbilical tension should be between 15-40
  N. Note that the tensions are reduced once the source is submerged.
\item \CheckBox[name=encp41]{} Move acrylic source to centre of detector (assuming source
  offset is 70 cm).
  \begin{center}
    \begin{tabular}{|l|l|}
      \hline
      console & \verb+manip > acrylic to 0 0 70+ \\
      \hline
      manmon & in acrylic window: \\
      & set x=0, y=0, z=70\\
      & click on {\bf move to} \\
      \hline
    \end{tabular}
  \end{center}      
\item \CheckBox[name=encp42]{} Take data. The exact configuration will vary.

  \begin{center} {\bf Retracting Manipulator to UI} \end{center}

\item \CheckBox[name=encp43]{} Contact Water Supervisor. Inform him/her that the source is
  about to be removed from the D$_{2}$O.
\item \CheckBox[name=encp44]{} Retract encapsulated source from AV into glovebox.
  \begin{center}
    \begin{tabular}{|l|l|}
      \hline
      console & \verb+manip > ambe to 0 0 1300+ \\
      \hline
      manmon & in ambe window: \\
      & set x=0, y=0, z=1300\\
      & click on {\bf move to} \\
      \hline
    \end{tabular}
  \end{center}
\item \CheckBox[name=encp44]{} Retract encapsulated source to posisition to disconnect side ropes
  \begin{center}
    \begin{tabular}{|l|l|}
      \hline
      console & \verb+manip > ambe to 0 0 1380+ \\
      \hline
      manmon & in ambe window: \\
      & set x=0, y=0, z=1380\\
      & click on {\bf move to} \\
      \hline
    \end{tabular}
  \end{center}
  {\it When moving the encapsulated source to 1380, it is important to make
    sure you are moving with respect to the {\bf pivot} and not the
    centre for the source which is approximately 70 cm below the
    pivot. This is especially important if the sideropes are
    attahced!}
  
  \begin{center} {\bf Retracting source above gate valve. Side ropes
      NOT attached.}
  \end{center}
  
\item \CheckBox[name=encp45]{} Move the encapsulated source to 1530
  \begin{center}
    \begin{tabular}{|l|l|}
      \hline
      console & \verb+manip > ambe to 0 0 1530+ \\
      \hline
    \end{tabular}
  \end{center}
\item \CheckBox[name=encp46]{} Move the encapsulated source to 1540
  \begin{center}
    \begin{tabular}{|l|l|}
      \hline
      console & \verb+manip > ambe to 0 0 1540+ \\
      \hline
    \end{tabular}
  \end{center}
\item \CheckBox[name=encp47]{} Move the encapsulated source to 1550
  \begin{center}
    \begin{tabular}{|l|l|}
      \hline
      console & \verb+manip > ambe to 0 0 1550+ \\
      \hline
    \end{tabular}
  \end{center}
      {\bf NOTE:\\
        MINIMUM SAFE HEIGHT TO CLOSE GATEVALVE IS 1535~cm.\\
        If unable to get above this height, contact expert.}
    \item \CheckBox[name=encp48]{} Retrieve the gatevalve key from the DCR lock box, if the
      gate valve handle is locked. Retrieve the handle from the DCR
      desk if the handle was removed.
    \item \CheckBox[name=encp49]{} Ready the gatevalve to be closed by unlocking or replacing
      the handle.
    \item \CheckBox[name=encp50]{} Carefully close the gate valve by rotating the handle {\bf
      clockwise}. {\it Expect resistance when the handle is about 3.4
      of the way to the closed position. This is the normal
      overcentering of the valve mechanism.} {\bf If resistance is
      felt before this or if any sounds are heard that might be caused
      by the valve hitting the source, STOP and contact and expert.}
      Record the time the valve is closed.

      \begin{center}
        \begin{tabular}{|l|}
          \hline \\ \TextField[name=tgvca,backgroundcolor=0.975 0.975 0.975,
        width=2cm]{Time Gate Valve Closed}\\
          \\
          \hline
        \end{tabular}
      \end{center}

    \item \CheckBox[name=encp51]{} Lock the gatevalve in the {\bf CLOSED} position.
    \item \CheckBox[name=encp52]{} Return the gatevalve key to the DCR lock box.
    \item \CheckBox[name=encp53]{} Record the Cover Gas O$_{2}$ level
      
      \begin{center}
        \begin{tabular}{|l|}
          \hline \\ \TextField[name=cgora1,backgroundcolor=0.975 0.975 0.975,
        width=2cm]{Time Gate Valve Closed}\\
          \\
          \hline
        \end{tabular}
      \end{center}

    \item \CheckBox[name=encp54]{} Close the URM flush valve if the source does not need drying
      out. {\it It is desireable to leave a minute flow of N$_{2}$
        through the URM in order to dry out the source and the
        umbilical. Contact OCE for instruction.}
    \item \CheckBox[name=encp55]{} Turn off the URM flush regulator (if the source does not
      need drying out).
    \item \CheckBox[name=encp56]{} If the laser is off, turn off the gas flow at the LN$_{2}$
      dear in the junction:
      \begin{enumerate}
      \item \CheckBox[name=encp57]{} close the {\bf Gas Use} valve.
      \item \CheckBox[name=encp1]{} close the {\bf Pressure Building} valve.
      \end{enumerate}
    \item \CheckBox[name=encp58]{} If the source is retracted, and gate valve closed, turn off
      gas flow at the high pressure LN$_{2}$ dewar in the junction:
      \begin{enumerate}
      \item \CheckBox[name=encp59]{} close the {\bf Gas Use} valve.
      \item \CheckBox[name=encp60]{} close the {\bf Pressure Building} valve.
      \end{enumerate}
      \begin{center} {\bf Afterr Calibration} \end{center}
    \item \CheckBox[name=encp61]{} Source is above gate valve.
    \item \CheckBox[name=encp62]{} Gate valve is closed and locked.
    \item \CheckBox[name=encp63]{} High pressure LN$_{2}$ dewar is turned off (bot {\bf Gas
      Use} valve and {\bf Pressure Building} valve) if source is not
      to be dryed out.
    \item \CheckBox[name=encp64]{} Flush return line is disconnected from rear of URM2.
    \item \CheckBox[name=encp65]{} Gas board is set up to provide sufficient flow to dry out
      the inside of the URM.
\end{enumerate}

% \end{form}

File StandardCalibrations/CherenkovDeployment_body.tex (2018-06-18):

\fancyhf{}
% \lhead{\begin{tabular}{|p{8.25cm}} \hline {\large \bf SNO+ Laser Procedures} \\ \\ \\ \\ \end{tabular}}
\lhead{\begin{tabular}{|p{8.25cm}|p{6cm}|}  
	\hline 
		{\large \bf SNO+ Cherenkov Calibration Procedure}  
										& Document No:  \\ 
								\cline{2-2} & Revision No: 01\\  
								\cline{2-2} & Effective Date: 2017-08-25\\ 
								\cline{2-2} & Page \thepage \\  \end{tabular}}

\begin{tabular}{||l|l|l||}
\hline\hline
& \multicolumn{2}{p{8cm}||}{\bf SNO+ Cherenkov Calibration Procedure} \\
 & \multicolumn{2}{p{8cm}||}{} \\
\hline
\multicolumn{2}{||p{8.5cm}|}{Document Number:} & Revision Number: 01\\
\hline
\multicolumn{3}{||l||}{Document Owner: SNO+ Calibration Post-Doc} \\
\hline
\multicolumn{3}{||l||}{Reviewer:}\\
\hline
Name: & Signature & Date \\
\hline
\multicolumn{3}{||l||}{Authorizer:}\\
\hline
Name: & Signature & Date \\
\hline\hline
\end{tabular}
\thispagestyle{empty}

\section{Purpose}

This procedure describes, step by step, the process of performing an
calibration using the Cherenkov source the centre of the detector in
single axis mode. It is intended as a guideline for operators who have
been trained on the manipulator and Cherenkov. It assumes that the Cherenkov
source is mounted on URM1, located on the 10" gatevalve on the UI
which is located on the south side of the UI.

\section{Outline of the procedure}

\begin{enumerate}
\item Prepare the URM for use (turn on N$_{2}$ supply etc.)
\item Flush URM1 with N$_{2}$ gas to remove room air and radon.
\item Calibrate URM1 central rope.
\item Lower source into UI.
\item Deploy source into detector.
\item Take $^{8}$Li data.
\item Retract source into source tube above gatevalve.
\item Shutdown N16 gas board and gas flow to URM.
\end{enumerate}
You will need the following procedures to complete an Cherenkov calibration.
\begin{itemize}
\item {\bf Cherenkov Calibration} (this procedure)\\ \\ \\ \\ \\
\item {\bf Central Rope Calibration Procedure} 
\item {\bf DT Generator Turn On Procedure} 
\item {\bf Cherenkov Source Startup Procedure}
\item {\bf Cherenkov Source Shutdown Procedure}
\item {\bf DT Generator Turn Off Procedure}
\end{itemize}

\section{Procedure}

\begin{tabular}{|l|l|}
\hline
\multicolumn{2}{|l|}{} \\
\multicolumn{2}{|l|}{\bf Cherenkov Calibration Procedure} \\
\multicolumn{2}{|l|}{} \\
\hline
& \\
\TextField[name=li8op,backgroundcolor=0.975 0.975 0.975,width=2cm]{Operator: } &
\TextField[name=li8d,backgroundcolor=0.975 0.975 0.975,width=4cm]{Date: } \\
& \\
\hline
\end{tabular}

The procedures in this section are intended to be followed sequentially for the Cherenkov calibration except where it is noted that a following step can be skipped. Specifically, if the Cherenkov is to be done in {\it single axis} mode, the side ropes do not need to be attached or detached from the source.

{\bf Prior to Cherenkov}

\begin{enumerate}
\item \CheckBox[name=li8p1]{} Permission for procedure and confirmation of equipment readiness has been received from the Head of the Calibration Group.
\item \CheckBox[name=li8p2]{} Cherenkov is mounted on URM1 which is mounted on the UI 10" gatevalve.
\item \CheckBox[name=li8p3]{} The gatevalve is closed and locked (or the handle is removed).

{\bf Readying Cherenkov Source and URM for Operation}

\item \CheckBox[name=li8p4]{} Contact Detector Operator and verify that the DCR activity bit is set.
\item \CheckBox[name=li8p5]{} Turn on lights in DCR following standard procedure.
\item \CheckBox[name=li8p6]{} Verify that the high pressure N$_{2}$ to the laser is valved off (end of laser, upper right hand corner). 
\item \CheckBox[name=li8p7]{} Verify that all valves on the gas board are closed and the regulator is set to zero.
\item \CheckBox[name=li8p8]{} Remove the flush return line on the URM. {\it The presence of the buffer line makes it difficult to measure the O$_{2}$ from the URM.}
\item \CheckBox[name=li8p9]{} Check that the flush inlet line is connected to URM1. If not connect it. Open the valve at the source tube. {\it It may be necessary to valve off the other URMs to get sufficient flow.}
\item \CheckBox[name=li8p10]{} Verify that the LN$_{2}$ dewar in the junction is at least 1/4 full. If not swap it out with another dewar. Record liquid level of dewar,
\begin{center}
\begin{tabular}{|c|}
\hline
\\
\TextField[name=li8n2l,backgroundcolor=0.975 0.975 0.975,width=2cm]{LN$_{2}$ Level:} \\
\\
\hline
\end{tabular}
\end{center}
\item \CheckBox[name=li8p11]{} Verify that the dewar gas pressure is above 20 psig. If not, swap it out with another dewar. Unlike the laser the $^16$N does not require a minimum of 100 psig N$_{2}$ is only used for flushing. Note that this dewar won't last long if the pressure is below 100 psig.
\item \CheckBox[name=li8p12]{} Turn on the high pressure N$_{2}$ flow from the dewar at junction (Marked {\bf Gas Use} on dewar).
\begin{center}
\begin{tabular}{|c|}
\hline
\\
\TextField[name=li8n2t,backgroundcolor=0.975 0.975 0.975,width=2cm]{Note Time:} \\
\\
\hline
\end{tabular}
\end{center}
\item \CheckBox[name=li8p13]{} Turn on pressure builder valve (Marked {\bf Pressure Builder} on dewar). {\it The pressure builder valve opens a controlled leak on the dewar to maintain the 150 psig pressure head. If the valve is not opened, the gas pressure to the laser and URM will eventually drop below the operating level (10 psig).}
\item \CheckBox[name=li8p14]{} Set up Gas Board in "bypass mode" for "URM flush" only. If you are using the high pressure feed {\bf do not exceed} 10 psi on the regulator. {\it Bypass mod maximizes the flow to the URM. (Gas enters at top left hand corner, flows through the regulator along the outside right hand side line down the URM with all other valves closed --- see the Gas Board Section for details)}.
\item \CheckBox[name=li8p15]{} Check that the flow meter (located at the east side of the pipe box) is railed. If not, open the needle valve near the flowmeter fully.\\ {\bf Flush should continue until O$_{2}$ reading at the rear of the URM is less than 0.8\%.} {\it This may take up to an hour depending on when the URM was last flushed.}
\item \CheckBox[name=li8p16]{} Once the URM is flushedd the N$_{2}$ supply may be switched from the high pressure dewar to the Wessington dewar. Check with the Operations Group first before switching. Do not use the Wessington if a transfer is in progress. Consult the gasboard section for details on how to switch. If the flush is continued from the high pressure deewar reduce the flow using the needle valve. A setting of 2 full turns above the point where the flowmeter rails is sufficient.
\item \CheckBox[name=li8p17]{} Verify (blue) valve on the LI8 Umbilical gas feed line (the translucent line is OPEN. If not, open it.
\item \CheckBox[name=li8p18]{} Execute the Cherenkov PMT Turn On Procedure.
\item \CheckBox[name=li8p19]{} Do not connect the PMT trigger cable to channel 4, slot 15 crate 17 before obtaining permission from the detector operator.
% \item \CheckBox[name=li8p20]{} Check that the source clamps are in the RELEASE position. There are two clamps. Check both. {\bf WARNING: The clamp positions RELEASE and HOLD are 90 deg apart. Rotate the clamp in the SHORT direction (90 deg) from the HOLD to RELEASE position. The clamp must not be rotated the other way!}\\ {\it The clamps are used to secure the source while the URM is being moved on and off the UI. If the source is moved with the clampes in the HOLD position, it may severely damage the manupulator and the umbilical.}
\item \CheckBox[name=li8p21]{} Check the pressure on the air cylinder for the umbilical takeup mechanism. It should be between around 55 psig. {\bf Do not operate the URM if the pressure is below 40 psig.} If the pressure falls below 10 psig at any point (even momentarily) call the OCE. An internal inspection of the URM is mandatory before operating the unit again. {\it The pressure cylinder on the URM maintains tension on the umbilical takeup reel. A low gas pressure can result in the umbilical falling off the takeup reel and getting caught or jammed leading to destruction of the umbilical.} 
\item \CheckBox[name=li8p22]{} Verify that the 10'' gate valve is closed and locked (or handle is removed). {\it The valve is CLOSED when the handle points towards the pipebox and the slot on the handle stem points AWAY from the source tube.} % Note this will change with the new gate valves
\item \CheckBox[name=li8p23]{} Calibrate Central Rope Length (see procedure {\it Central Rope Position Calibration}). Record changes in length of central rope and umbilical. The current fiducial mark for URM1 on gatevate 3 is 
\[
z_{mark} = 1548.95
\]
Note: the fiducial mark is written on the source tube. If it differs from the above number use what is written on the source tube.
\begin{center}
\begin{tabular}{|c|}
\hline
\\
\TextField[name=li8dl,backgroundcolor=0.975 0.975 0.975,width=3cm]{$\Delta l$ rope:}\\
\\
\hline
\\
\TextField[name=li8du,backgroundcolor=0.975 0.975 0.975,width=2cm]{$\Delta l$ umbilical:}\\
\\
\hline
\end{tabular}
\end{center}
\item \CheckBox[name=li8p24]{} Check that all seals are in place on the URM. Including:
	\begin{itemize}
	\item \CheckBox[name=li8p24a]{} flush inlet line
	\item \CheckBox[name=li8p24b]{} window on front of URM motorbox
	\item \CheckBox[name=li8p24c]{} window on rear of URM motorbox
	\item \CheckBox[name=li8p24d]{} umbilical feedthrough on rear of motorbox
	\item \CheckBox[name=li8p24e]{} view port window cover on source tube
	\item \CheckBox[name=li8p24f]{} window on rear of stretcher box
	\end{itemize}
{\it Note that the flush outlet is small enough and is small enough that it does not pose a threat to the detector unless light is shone directly into it.}
\end{enumerate}

{\bf Deploying Source from Source Tube Into Glovebox}
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

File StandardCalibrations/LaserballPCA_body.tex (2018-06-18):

\fancyhf{}
% \lhead{\begin{tabular}{|p{8.25cm}} \hline {\large \bf SNO+ Laser Procedures} \\ \\ \\ \\ \end{tabular}}
\lhead{\begin{tabular}{|p{8.25cm}|p{6cm}|}  
	\hline 
		{\large \bf SNO+ Laser Ball PCA Procedures}  
										& Document No:  \\ 
								\cline{2-2} & Revision No: 01\\  
								\cline{2-2} & Effective Date: 2017-06-14\\ 
								\cline{2-2} & Page \thepage \\  \end{tabular}}

\begin{tabular}{||l|l|l||}
\hline\hline
& \multicolumn{2}{p{8cm}||}{\bf SNO+ Laser Ball PCA Procedures} \\
 & \multicolumn{2}{p{8cm}||}{} \\
\hline
\multicolumn{2}{||p{8.5cm}|}{Document Number:} & Revision Number: 01\\
\hline
\multicolumn{3}{||l||}{Document Owner: SNO+ Calibration Post-Doc} \\
\hline
\multicolumn{3}{||l||}{Reviewer:}\\
\hline
Name: & Signature & Date \\
\hline
\multicolumn{3}{||l||}{Authorizer:}\\
\hline
Name: & Signature & Date \\
\hline\hline
\end{tabular}
\thispagestyle{empty}

\section{Purpose}

The calibration of the SNO+ PMTs requires a standardized light source. The standardized light is provided by a dye laser coupled to the laserball which may be deployed into the detector AV. 

\section{Supporting Procedures}

This procedure may be supplemented by documents available from the SNO calibration home page
\url{http://www.sno.phy.queensu.ca/private/calibration/index.html}.
These procedures will be reviewed as necessary.\\

{\bf Online Manipulator Documentation} Contains online manual for all commands and operations with the manip program running on the calibration computer. This is the reference source for commands done from the manip console.\\

{\bf Manipulator User Manual} Contains an overview of the manipulator system and descriptions of sources and some procedures. In particular it describes how to start the manmon program for controlling and monitoring the manipulator.\\

{\bf Manipulator Reference Manual} contains technical information on the manipulator.\\ \\ \\ \\ \\ 

\section{Outline}
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

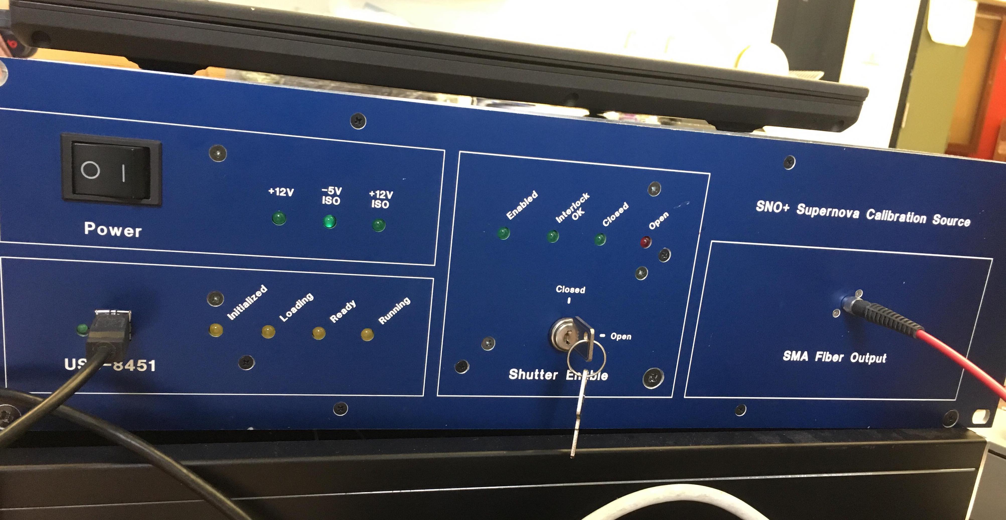
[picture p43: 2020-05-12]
SuperNovaCalibrationSource/SupernovaSource.jpg

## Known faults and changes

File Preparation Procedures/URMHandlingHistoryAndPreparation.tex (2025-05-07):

\documentclass[11pt]{article}

\usepackage{geometry}                % See geometry.pdf to learn the layout options. There are lots.
\geometry{letterpaper}                   % ... or a4paper or a5paper or ... 
%\geometry{landscape}                % Activate for for rotated page geometry
%\usepackage[parfill]{parskip}    % Activate to begin paragraphs with an empty line rather than an indent
\usepackage{graphicx}
\usepackage{amssymb}
\usepackage{epstopdf}
%\usepackage{enumitem}
\usepackage{ulem}
\usepackage{verbatim}
\usepackage{hyperref}
\DeclareGraphicsRule{.tif}{png}{.png}{`convert #1 `dirname #1`/`basename #1 .tif`.png}
\usepackage{caption}
\usepackage{subcaption}

\usepackage{pifont,amssymb} % for the symbols
\usepackage[shortlabels]{enumitem}

\newlist{answerlist}{enumerate}{2}
\setlist[answerlist]{label={\arabic*.\makebox[0pt][r]{\noexpand\emptysquare\hspace{2em}}},ref=\alph*}

% \newlist{subitemlist}{enumerate}{2}
% \setlist[subitemlist]{label={\alph*.\makebox[0pt][r]{\noexpand\emptysquare\hspace{2em}}},ref=\alph*}

% \newlist{itemlist}{itemize}{2}
% \setlist[answerlist]{label={\alph*.\makebox[0pt][r]{\noexpand\emptysquare\hspace{2em}}},ref=\alph*}

\newcommand{\emptysquare}{$\square$}
\newcommand{\checkedsquare}{\makebox[0pt][l]{\raisebox{1pt}[0pt][0pt]{\large\hspace{1pt}\cmark}}$\square$}
\newcommand{\cmark}{\ding{51}}%
\newcommand{\correctanswer}{{\renewcommand{\emptysquare}{\checkedsquare}\item\leavevmode}}

\title{URM Handling, History, and Preparation}
\author{Ryan Bayes}
\date{\today,\\ Version 6}

\begin{document}
\maketitle

The URM (umbilical retrieval mechanism) is central to the calibration deployment project. With the requirements for scintillator compatibility and controlling backgrounds, the URM was redesigned with these constraints in mind. The principle difference is that the scintillator URMs are designed to have an isolated nitrogen gas volume to reduce the likelihood of radon ingress to the UI (universal interface) resulting from deploying a source. Specific design elements were also changed to make the isolation of the URM sustainable.

\begin{figure}
  \begin{center}
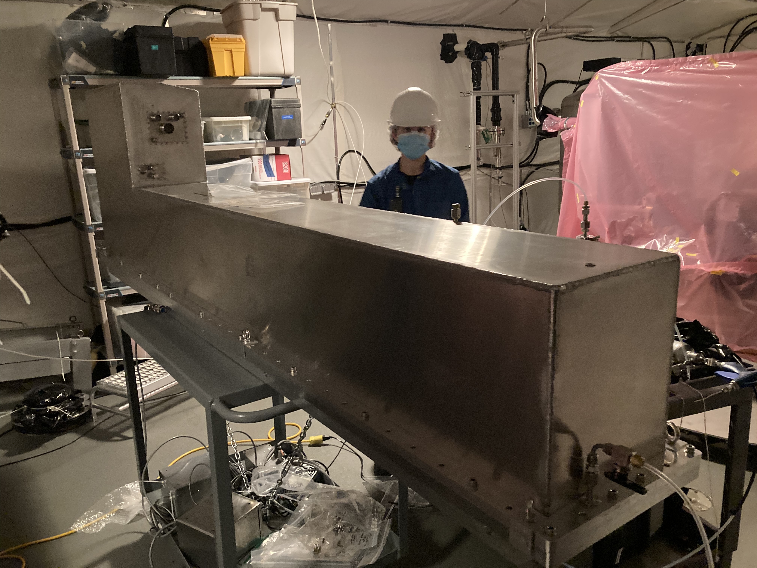
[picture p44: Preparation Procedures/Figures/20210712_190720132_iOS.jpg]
    
  \end{center}
  \caption{The Scintillator URM to be used for the source deployment}
  \label{fig:URM4}
\end{figure}

The following document describes the history of commissioning the URM at SNOLAB prior to describing how the URM must be prepared. This covers running the electrical subsystems checks, preparing the umbilical feed-through plate, the umbilical installation, the rope installation, the source connector installation, the cover installation, the source tube and bellows installation, the gatevalve installation, The final umbilical cleaning, the cover gas connection, and a test deployment procedure. The document concludes with a proposed order of operations and scheduling is shown at the end of the document.

\section{Definitions}
\begin{itemize}
\item AV: The acrylic vessel. A 12~m diameter acrylic sphere, fabricated for SNO, that currently contains the SNO+ scintillator cocktail.
\item PSUP: Photo-multiplier support structure. A geodesic sphere with an average diameter of 17~m, that supports the $\sim$9400 PMTs used to detect light in the SNO+ experiment.
\item Umbilical: a 1/2'' cable made by potting a HDPE tube surrounded by electrical wires inside a Tygothane tube using SilGel. The umbilical used here has a fibre optic bundle inside the HDPE core.  
\item Rope: 1/8'', white, braided, Tensylon fibre cord that has been shown to have good strength characteristics while being compatible with LAB. The central rope is installed on the URM while side ropes are made of the same material inside the AV. 
\item Calibration Source or Source: An item that can be deployed inside the scintillator volume that generates a known signal used to interpret the detector response. A dummy source will also be used which produces no signal, but will be used to test the manipulator system response.
\item URM: Umbilical retrieval mechanism. A device containing the umbilical and the central rope equipped with motors to deploy and retract both simultaneously and load cells to monitor the tension on the rope and umbilical. The umbilical is stored on a pair of pulley blocks connected to a charged piston that forces the blocks apart as the umbilical is retracted into the system. The rope is stored on a rotating drum.
\item UI: Universal interface. A 1.3 m diameter stainless steel vessel designed to contain a nitrogen cover gas over the SNO+ scintillator volume at the top of the AV neck. Equipped with a number of access points to deploy sensors, recirculate scintillator and deploy calibration sources.
\item DCR: Deck clean room. A tent on the SNO+ deck with additional HEPA filters to produce a clean environment for preparing calibration sources, or otherwise interaction with the AV interior. 
\item Source Bellows: A flexible stainless steel structure meant to connect the URM to the UI while allowing for the free movement of the UI. Must be terminated with a gatevalve. 
\item URM Hangers: Horizontal beams fixed to the DCR lifting beam. Includes rollers to allow for the limited use of lifting straps as well as turnbuckles to provide partial, semi-permanent support for the URM on rails
\item URM Lifting Table: table rated to lift 798 kg with an 80-20 paired frame with an interior hydraulic lifting system to raise the URM an additional 30~cm
\item URM Lifting System: Assembly of the URM hangers (specifically the lifting straps and winch) and the URM lifting table. It is essential that these be used in concert for stability when lifting the URM to height. 
\end{itemize}

\section{History}

\subsection{Arrival at SNOLAB, Cleaning and Testing, February 2017 - March 2019}
General comments about the handling: all operations with the URM were conducted in a cleanroom setting after the URM was placed in the SNOLAB cleanrooms and it was not removed from the cleanroom until after it was disassembled and bagged prior to being shipped underground. General guidelines were that the URM was never handled without cleanroom gloves on the hands of the workers and that the URM was cleaned after every interaction with UPW and Kimwipes. 
\begin{itemize}
\item {\bf June - August, 2017} URM completely disassembled, cleaned and reassembled. All large pieces were completely wiped with UPW. Screws were ultrasonically cleaned. 
\item {\bf August - September, 2017} Electrical systems and wiring for motors and sensors setup. Installed a rope to facilitate slipping and stretching measurements.
\item {\bf November 2017} Installed umbilical \#5 on URM after wiping down umbilical and URM with kim wipes and UPW (there was dust observed on the Umbilical).
\item {\bf June - August, 2018} Rope stretch tests in air, UPW and LAB. The contaminated rope was removed and never retracted into the URM.
\item {\bf August, 2018} Umbilical tests including running rope and umbilical together and umbilical slip tests (the umbilical did not slip under tensions up to 200 N).
\item {\bf September, 2018} Leak checked internal gas distribution systems to exclude leak rates above 10$^{-8}$ mbar L/s.
\item {\bf November 2018} Expanded the hole in the retraction pulley to accept an M4 eye-bolt.
\item {\bf January - September 2019} Redo rope stretch tests in air. 
\item {\bf September 2019} Installed limit switches at either end of
  the URM track.
\end{itemize}

\subsection{Transport Underground, January 2020}
See Cindy Lin's document on the preparation of the URM and conclusion of the transport underground, DocDB \href{https://www.snolab.ca/snoplus/private/DocDB/0061/006139/002/URM4_Final_Packing__Transporting_UG__and_DCR_Cleaning.pdf}{6139}. The summary is that the URM was disassembled, and all components were triple bagged before being crated up for transport underground. Once underground, the bags were systematically wiped down and removed starting with the outer layer in the outer car-wash, and the middle layer in the inner car wash before storage in the DCR. 

\subsection{Commissioning Underground to Date, May 2021 - August 2021}
\begin{itemize}
\item {\bf May 2021} Reassembled URM inside DCR. Surface cleaned parts by hand with Kimwipes and UPW. Some minor test of the electrical systems and reviewed the changes made to the limit switches.
\item {\bf July - September 2021} Leak check internal gas distribution components and cover flange. Installed externally flanged VCR ports and vents with gaskets.
\end{itemize}

\section{Remaining Procedures}

\subsection{Order of Operations}

The following procedures are described in by order of association, and not the practical order. To in fact assemble and commission the URM the processes should be done in the following order. 
\begin{answerlist}
\item Preparation of umbilical feed-through plate; Sec.\ref{ss:umbPrepFeed} (1 shift, machine shop?)
\item Remove URM cover; Sec.\ref{ss:rmCov} (1 shift, 4 workers)
\item Electrical systems check; Sec.\ref{ss:elecSSC} (1 shift, 1 worker)
\item Clean the umbilical; Sec.\ref{ss:cleanUmb}
\item Clean the surfaces of the pulley blocks and drive pulleys; Sec.\ref{ss:cleanURM}
\item Install umbilical on URM; Sec.\ref{ss:UmbInstall} (1 shift, 3 workers)
\item Install umbilical feed-through plate on umbilical; Sec.\ref{ss:umbPrepFeed} (1 shift, 2 workers)
\item Install rope on URM; Sec. \ref{ss:RopeInstall} (1 shift, 2 workers)
\item Install URM cover; Sec.\ref{ss:CoverInstall} (1 shift, 4 workers)
\item Transfer URM from cart to lifting table; Sec.\ref{ss:transfer} (1 shift, 6 workers)
\item Electrical systems check; Sec.\ref{ss:elecSSC} (1 shift, 1 worker)
\item Install source tee flange; Sec.\ref{ss:SourceTeeInstall} (1 shift, 2 workers)
\item Epoxy the fibre bundles at both ends of the umbilical;
\item Install source connector on umbilical; Sec.\ref{ss:SourceConn} (1 shift)
\item Final Umbilical cleaning; Sec.\ref{ss:UmbClean} (1 week)
% \item Install the wheels on the URM; 
\item Install source bellows; Sec.\ref{sss:BellowsInstall}
\item Install gate valve; Sec.\ref{sss:GateValveInstall}
\item Purge the URM and connect to the cover gas system; Sec.\ref{ss:CGConnection}
\item Connect and clean the AmBe source (?) (1 week, 3 workers)
\item Connect URM to UI; Sec.\ref{ss:CGConnection} (1 shift, 3 workers)
\item Field test the manipulator system.; Sec.\ref{ss:Testing} (1 shift, 3 workers)
\end{answerlist}
The listed time and personnel requirements are estimates to within the nearest shift. Many of these tasks and procedures may take fractions of shifts, but there are few procedures that can be done in parallel; primarily tasks that affect completely different aspects of the URM without overlap.

\subsection{General Comments}
For all of the following procedures workers must keep the following points in mind.
\begin{itemize}
\item Workers must use proper PPE for working in the underground clean lab
\item All procedures are to be conducted in the DCR.
\item Assume that nitrile clean room gloves are to be worn at all times.
\item When working on the interior workings of the URM
  \begin{itemize}
  \item Double gloves must be worn. Inside and outside gloves should be rinsed with UPW after they are donned.
  \item After handling lubricants or oils, the outer gloves must be removed and replaced.
  \end{itemize}
\item Every effort must be made to maintain the integrity and cleanliness of the DCR.
\item When the inner workings of the URM are exposed to the DCR, the dust counts should be monitored. Prior to work beginning, the number of 0.5$\mu$m particles must be less than 200 per cubic foot.
\item Workers must change coveralls if they work in specific locations prior to conducting work in the DCR including the underground machine shop and the inner car-wash.
\item Workers must shower and change clothes if they work in specific locations prior to working in the DCR including the scintillator plant and the outer car-wash. 
\end{itemize}

\subsection{Personal Protective Equipment: Donning Gloves}\label{ss:Rgloves}
The general glove cleanliness protocol requires that operators exercise extreme care when handling equipment that will come into contact with the detector scintillator.
\begin{answerlist}
\item Thoroughly wash and dry hands.
\item Put on a pair of clean room nitrile gloves.
\item Spray with UPW and rub hands together.
\item Rinse with UPW.
\item Dry with Kimwipe.
\item Put another pair of clean room nitrile gloves.
\item Spray UPW on the clean room gloves and rub hands together.
\item Rinse with UPW.
\item Dry with Kimwipe.
\end{answerlist}

\subsection{Removing the URM Cover}\label{ss:rmCov}
The first step to the majority of the activities to commission the URM is to remove the cover. The URM has been stored with the cover on to protect it from dust contamination. 
\begin{answerlist}
\item Remove the screws from the electrical and umbilical feed-through plates. Carefully remove the feed-through plates from the URM cover.
\item With an M5 hex and crescent wrench, remove the bolts holding the URM cover flange to the base. Store the nuts, bolts and washers so that they can be easily found and used. 
\item Ensure that the support feet and eye-bolts are secured to the flange at the four corners of the URM cover.
\item Prepare an area out of the way of other activities to place the URM with a piece of plastic suitable to be wrapped over the URM cover.
\item With four workers; one at each corner; with an appropriate height assist, lift the URM cover straight up off of the URM flange until it is clear of the URM backplane.
\item Carefully lower the URM cover onto the prepared plastic sheet. Wrap the sheet over the URM cover.. 
\item Check the URM o-ring. Ensure that it remains in its groove with no obvious damage.
\item Install the bumpers on the URM flange to protect both the URM flange surface and the o-ring using the same bolts as those that secured the cover to the base. 
\end{answerlist}

\subsection{Electrical Subsystems Check}\label{ss:elecSSC}
It is essential that the electrical systems be checked periodically
through this procedure to ensure that there is no loss of
function. The 20 pin feed-through is somewhat fragile and is easily
put under strain when the cover is removed or replaced. Tests must be
conducted with a manipulator control unit, and URM power
supplies. Tests should be conducted with the URM cover removed.

Running the electrical system requires
\begin{itemize}
\item A Special paired cable connecting to a single 20 pin Amphenol connector at one end and a pair of DB-15 bus connectors on the others
\item A AVR control box shown in fig. \ref{fig:AVRUnit}
\item Two Motor power supply boxes; each must have a power cable and a 6 pin Amphenol connector terminated output cable integrated into the box.
\item Two four pin motor control cables
\item One AVR power supply
\item An extension sufficient to reach the Manip computer in the DCR garage
\item The URM with the cover off.
\end{itemize}

\begin{figure}
  \begin{center}
    
  \end{center}
  \caption{The box containing the AVR controller boards that are to be used with URM4}
  \label{fig:AVRUnit}
\end{figure}

\begin{enumerate}[label={$\square$}]
\item Connect the components as shown in Fig. \ref{fig:controller}.
  \begin{itemize}[label={$\square$}]
  \item The Rope and Umbilical sense cables attach to the URM via the
    20 pin socket mounted to the electrical feed-through plate,
  \item the DB-15 ends of the Rope and Umbilical sense cables connect
    to the AVR Unit via the appropriate socket. Convention has the
    Umbilical on the bottom and the rope on the top connector, but
    this should be verified with the Manip configuration on the
    Calibration Computer.
  \item The 6 pin Amphenol terminated control cables connect to 6 pin
    sockets, when looking at the feed-through plate from the outside,
    the umbilical motor control cable should be connected to the right
    feed-through socket and the rope connected to the left feed-through
    socket.
  \item The two four pin motor control cables run between the AVR
    control unit and the the motor power supply units.
  \item Connect the USB cable to the Manip computer USB extension,
    usually kept on the Northwest side of the UI.
  \item Plug the motor power supplies and the AVR power supply into an
    extension cable. Ensure that the fan is running on the AVR power
    supply. Make sure that the power switches on the motor supplies
    are set to on and the red LED lights are illuminated.
  \item Connect the AVR box to the computer power supply via the bus
    cable connector on the top of the AVR box. Ensure that the fan
    still runs after connecting the power supply and that the green
    LED light inside the AVR box is illuminated.
  \end{itemize}
\item Go to the Calibration computer and check if the appropriate AVR board
  is connected.
  \begin{itemize}[label=$\square$]
  \item Open a terminal and navigate to the \verb+AVR32+ directory
  \item Run the command \verb+manip+
  \item At the \verb+manip+ command prompt run \verb+init+
  \item Check the list of connected AVRs. Ensure that the AVR connected to URM4 appears in the list.
  \item Run the command \verb+show laserball+ on the command prompt. Disconnect URM2rope and URM2umbilical from the Laserball using the \verb+laserball disconnect+ command if necessary.
  \item In manip, connect the URM4rope and URM4umbilical objects to
    the Laserball source and check if the URM is receiving feedback on
    the load cells. If not the system will need to be debugged,
    starting with ensuring that the correct AVR connects to the the
    URM4rope and URM4umbilical objects in the \verb+WIRING.dat+ file
    in the \verb+AVR32+ directory
  \item Run the rope and umbilical by running the motors directly from
    the manip interface.
  \item Test the limit switches by moving the retraction block to either
    end of the track. If the limit switch signals are not detected by
    the manip interface, the reason must be understood and corrected.
  \end{itemize}
\end{enumerate}

\begin{figure}
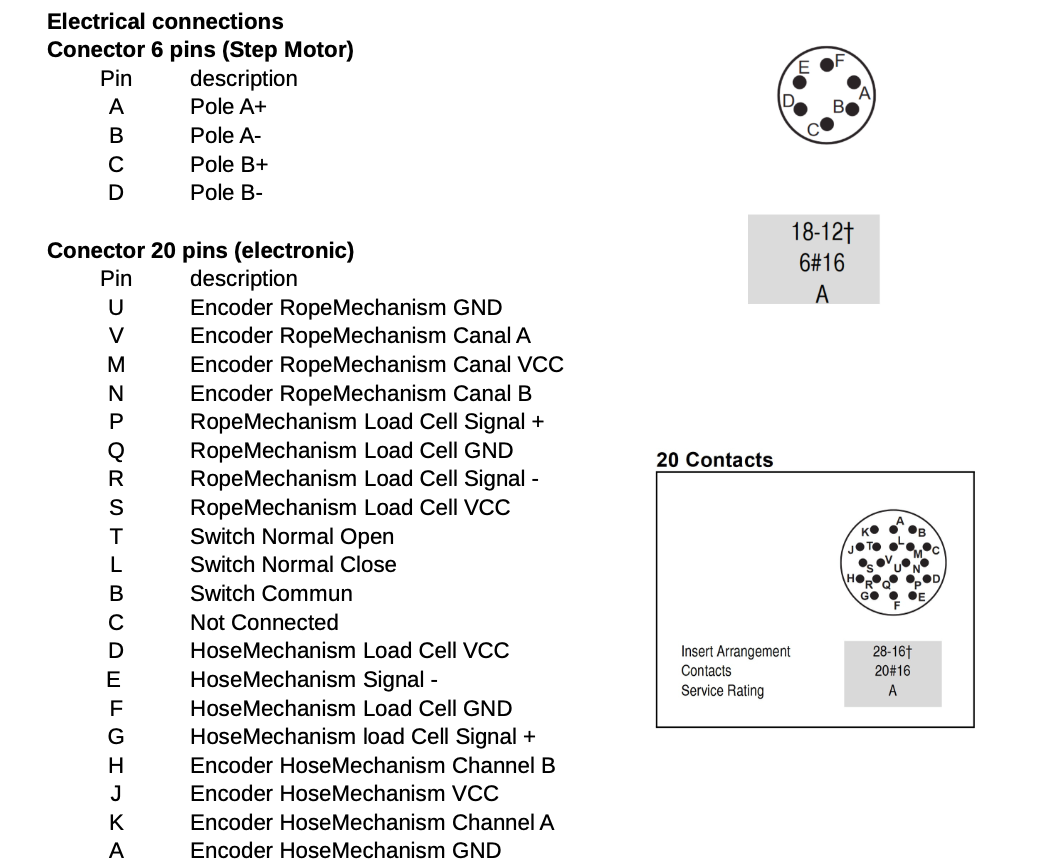
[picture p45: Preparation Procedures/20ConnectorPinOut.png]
  
  \caption{Pin out diagram for the URM as of August 2017. One minor revision made to incorporate the limit switch circuits in 2021.}
  \label{fig:pinout}
\end{figure}

\begin{figure}
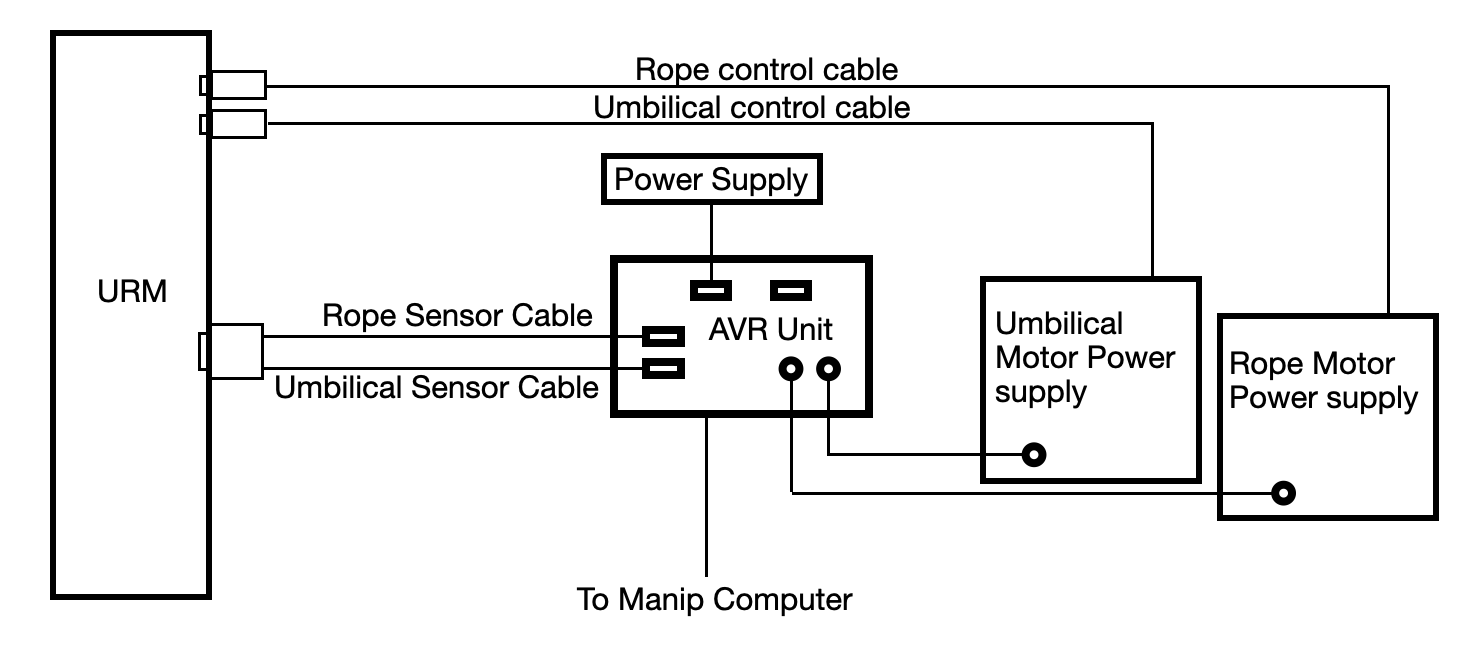
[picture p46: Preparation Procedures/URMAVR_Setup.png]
  
  \caption{Diagram of AVR controller setup for URM.}
  \label{fig:controller}
\end{figure}

\subsection{Cleaning the Umbilical}\label{ss:cleanUmb}
The umbilical to be used is the 8th scintillator umbilical assembled
at Queen's in 2016. This is the only umbilical synthesized with a
fiber optical bundle. The umbilical was wiped once with acetone, then
with methanol in the Queen's clean lab and stored in a clean bag
inside of a nitrogen filled mylar bag. From 2017 to 2024 the umbilical
in its bag in the bottom of a cabinet in SNOLAB cleanroom A. It was
moved from the cleanroom as the Diol still commissioning ramped up and
is sitting on a desk with two additional plastic bags over the mylar
bag. Prior to further installing the umbilical on the URM, the
umbilical must be cleaned. For this procedure it is assumed that the
following materials are on hand in the DCR
\begin{itemize}
\item The umbilical in its original mylar bag
\item A spill tray suitable to catch LAB
\item A supply of clean LAB
\item A supply of UPW
\item Nitrile, clean-room gloves
\item poly gloves 
\item fisher-brand, Poly-cellulose cleanroom wipes (should start with an unopened pack)
\item Two clean plastic bag suitable made from pink static resistant plastic (inside the DCR).
\item A heat sealer
\item A nitrogen source (using a standard bottle on deck) with a regulator and a flow meter.
\end{itemize}
Cleaning the umbilical is to be done in a two step process. This
should be done between three workers; two to handle the umbilical and
one to provide additional help or go for additional items if needed. The first step provides an initial starting point for the cleanliness of the umbilical, while the second step prepares the umbilical for loading on the URM. To initially clean and evaluate the state of the umbilical
\begin{answerlist}
\item Prepare a spill tray by wiping it out with UPW and lint free
  cloths. Similarly clean the beige working tray and put it to one
  side.
\item Don clean-room gloves using the procedure in section \ref{ss:Rgloves}
\item Open the top of the umbilical storage bag. 
\item With one worker holding the bag, pull the umbilical from the bag
  and place it in one corner of the spill tray.
\item Inspect the outside of the umbilical for damage.
\item Pick out one end of the umbilical. Shine a light into the one
  end of the umbilical and look for the light at the other end. The
  light should be visible at the ends of the fibers on the opposite
  end, even though the bundle is not yet complete. Count and record
  the illuminated fibers.
\item Designate one end of the umbilical as the standing end. This
  will be the end of the umbilical that will be secured to the URM
  umbilical feed-through. Both the standing end and the running end of
  the umbilical (the end to which the source will be connected) are
  identical and the fibre bundles will need to be terminated after
  loading onto the URM (the procedure of which will be communicated
  elsewhere).
\item Protect the ends of the umbilical. This can be done by wrapping
  the end in plastic wrap, or a plastic sleeve held in place with a
  zip tie. It is expected that the ends of the fibers are flush with
  the ends of the umbilical at this time, so this will mostly
  protect the fibers as they flex during installation. Cap the standing
  end of the umbilical with a different colour sleeve relative to the
  running end.
\item Wet a lint free cloth with UPW.
\item Starting with the running end, wipe the umbilical in strokes
  towards the standing end with UPW. Coil the umbilical in the
  opposite side of the spill tray. Be sure to keep an eye out for
  kinks and possible surface damage to the umbilical throughout this
  process.
\item Once the entire umbilical has been wiped down transfer the umbilical to a clean pink plastic bag.
\item Insert an open line to the nitrogen source into the bag with an outlet line. Seal the plastic bag with the heat sealer so the inlet and outlet lines are contained. Open the valve to the nitrogen supply with an output pressure on the order of 20 psi at a flow rate of 5 L/min. This will dry out the umbilical in a contained way. Leave the umbilical in this configuration overnight.
\item After drying the umbilical completely, open the bag and place the umbilical in the spill tray. Take tape lifts from various locations along the length of the umbilical and submit the tape lifts for XRF analysis. 
\item Return the umbilical to the plastic bag. Fill the bag with nitrogen and heat seal the bag.
\item Store the umbilical in a bin to protect the bag until use. 
\end{answerlist}
A second cleaning procedure should be followed immediately prior to loading the umbilical onto the URM; ideally in the same shift. Again this procedure should be completed by two workers with a third in reserve to handle 
The two workers must take the following 
\begin{answerlist}
\item Prepare a spill tray by wiping it out with UPW and lint free
  cloths. Similarly clean the beige working tray and put it to one
  side.
\item Don clean-room gloves using the procedure in section \ref{ss:Rgloves}
\item Open the top of the umbilical storage bag. 
\item With one worker holding the bag, a second should pull the
  umbilical from the bag and place it in one corner of the spill tray.
\item Inspect the umbilical again. Pick out one end of the
  umbilical. Shine a light into the one end of the umbilical and look
  for the light at the other end. The light should be visible at the
  ends of the fibers on the opposite end, even though the bundle is
  not yet complete. Count and record the illuminated fibers.
\item Wet a lint free cloth with clean LAB.
\item Identify the running and standing ends of the umbilical 
\item Protect the ends of the umbilical. This can be done by wrapping the end in plastic wrap, or a plastic sleeve held in place with a zip tie. It is expected that the ends of the fibers are flush with the ends of the umbilical at this time, so this will mostly protect the fibers as they flex during installation. 
\item Starting from the running end of the umbilical, wipe the
  Tygothane surface of the umbilical with the LAB wetted cloth with
  multiple passes on each section. Coil the umbilical loosely as you
  go in the opposite corner of the spill tray.
\item Once you get to the standing end of the umbilical, Store the
  cloth used to wipe the umbilical for particle counting analysis, and
  change outer gloves to use a new, clean pair.
\item Wet a new lint free cloth with clean LAB.
\item Flip the coil of umbilical over to access the running end again
  and, wipe the Tygothane surface of the umbilical with the LAB wetted
  cloth using multiple passes for each section. Coil the umbilical
  loosely in the corner of the spill tray opposite to that where it
  was coiled as you go.
\item Once complete, leave the standing end of the umbilical available
  for installation on the URM and cover the umbilical loosely with the
  beige spill tray. Store the outer gloves in a bag for appropriate
  disposal. Store the LAB wetted cloth for particle counting analysis.
\end{answerlist}

\subsection{Cleaning the URM (prior to umbilical installation)}\label{ss:cleanURM}
At each stage of the URM assembly, disassembly, movement underground and reassembly, the components of the URM have been cleaned with UPW and cleanroom wipes. The last opportunity to clean the URM before source deployment will be after the URM cover is removed and before the umbilical is installed. To clean the URM two workers will require
\begin{itemize}[label=$\square$]
\item a fresh supply of UPW
\item two spray bottles
\item a fresh pack of Fisherbrand, Poly-cellulose cleanroom wipes
\item supply of cleanroom gloves.
\end{itemize}
To clean the URM the workers must
\begin{answerlist}
\item Don clean room gloves using the procedure in section
  \ref{ss:Rgloves}.
\item Remove the front and rear pulley blocks, The umbilical motor
  assembly, the rope encoder pulley, and the sprung rope pulley.
\item Disassemble the front and rear pulley blocks, the rope encoder
  pulley, and the sprung rope pulley. Remove the guide and drive
  pulleys from the umbilical motor assembly. Be careful removing the
  bearings from the guide pulleys in particular as there is some
  potential for grease on the surfaces. Note that no grease was
  observed on the outside surfaces of the bearings from the
  disassembly of URM5, but some caution is warrented.
\item Clean the umbilical motor assembly with UPW and clean room
  wipes.
\item Mist the remaining surfaces of the URM and wipe the surface with
  the cleanroom wipes until the surface is again dry. This should
  include the URM backplane, support braces, bed, piston, and
  retraction pulley. Special care should be taken to wipe the bottom
  rope pulleys with UPW as it is extremely difficult to remove those
  pulleys from the system for ultrasonic cleaning without removing the
  back plane.
\item Reassemble the front and rear pulley blocks, the rope pulleys,
  and the pulleys on the motor assembly using the parts from
  URM5. URM5 is physically identical to URM4, and the pulleys and
  their support systems have already been cleaned ultrasonically, so
  the blocks, and rope pulleys can just be replaced. Similarly the
  pulleys on the URM4 motor assembly should be replaced with the clean
  ones from URM5.
\item Wipe down the traveling pulley and bottom pulleys with UPW and
  clean room wipes. Use a standard swip test on the working surfaces
  of the pulleys to ensure that there is no evidence of grease
  remaining. If there is grease, clean the surface with isopropyl
  alchohol, before again cleaning with UPW and wipes.
\item Start the rope motor at low speed (50 rpm) to facilitate
  cleaning the rope drum. Use compact cotton swabs to get inside the
  rope groove on the rope drum and check to make sure that there is no
  residue on the swab it proceeds from the top of the groove to the
  bottom. If there is evidence of grease, wipe out the groove of the
  rope drum again with isopropyl alchohol and lint free wipes before a
  last pass with UPW and lint free wipes.
\item Replace the ultrasonically cleaned rope and umbilical pulley
  blocks. Replace the motor assembly with the cleaned pulleys
  installed.
\item Reconnect all of the system cabling (where necessary) and
  conduct a full electrical systems check.
\end{answerlist}
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

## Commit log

2017-06-15 Create LaserballPCA.tex
    Added revision history to PCA description
2017-07-04 Minor corrections to the Laserball PCA procedures.
2017-08-14 Updates to laserballPCA instructions and added manipulator instructions.
2017-08-29 Committing N16 calibration procedures and moving laserball calibration to the same directory
2020-04-08 adding further refactored material and overview sections
2022-02-17 Initial procedure for laser ball scintillator
    Skeleton of deployment procedure for laser ball in scintillator. Formatting still to be done. Will also need to check the procedure against the hardware as built.
2022-02-22 Formatted Laserball PCA
    Introduced tabular formatting for the procedure. Separated out the procedure into sections.
2022-07-08 Adding sample umibilical cleaning pdf
2025-03-21 Adding preparation procedures, with a particular emphasis on the URM handling procedures
    [SNO+Mockup.FCStd, UmbilicalFeedthroughPlateMockup.FCStd]
2025-04-30 Adding Jamie's procedure for making the fibre bundle during source connector installation.
